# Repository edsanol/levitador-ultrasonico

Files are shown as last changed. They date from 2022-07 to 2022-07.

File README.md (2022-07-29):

# levitador-ultrasonico

El presente proyecto expone el diseño y la construcción un levitador capaz de hacer 
suspender partículas en el aire a través del principio de las ondas 
electromagnéticas, en este caso, las ondas acústicas mediante transductores 
ultrasónicos; con este principio, una partícula se levitará en contra de la fuerza de 
gravedad por medio de la presión sónica generada y alcanzará el equilibrio al 
contrarrestasen las ondas estacionarias. Además de esto, mediante un sistema de 
control clásico discreto, se realizará control de posición de las partículas en dos 
dimensiones (X, Z) al posicionar dos levitadores perpendicularmente haciendo 
necesario que el centroide de ambos sea común y se hará monitorización a través 
de un sistema HMI usando una cámara y visión artificial, quien detectara la posición 
de la partícula en las dos dimensiones. 

El proyecto inicia con el estudio del fenómeno detrás que la levitación acústica, 
dando a entender el por qué y las condiciones para hacer levitar objetos de mayor 
tamaño, seguidamente de esto, se diseña el modelado en donde se observa el 
posicionamiento de los transductores y las cotas del prototipo, a continuación, se 
realizan las pruebas de levitación de partículas en el prototipo. Una de las secciones 
fundamentales para el control de posición de partículas, es la implementación de la 
visión artificial, responsable de localizar y calcular la posición de la partícula los ejes 
X y Z; por último, se implementa un control clásico PID para controlar la posición de 
las partículas en el levitador que será supervisado por una interfaz humano maquina 
HMI.

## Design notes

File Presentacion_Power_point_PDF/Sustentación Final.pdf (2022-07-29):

# DESARROLLO DE UN SISTEMA DE CONTROL DE POSICIÓN DE PARTÍCULAS CON VISIÓN ARTIFICIAL EN UN LEVITADOR DE ONDAS ULTRASÓNICAS

# Autor: EDINAEL SANGUINO OLIVARES Tutor: M.Sc. OSCAR MANUEL DUQUE SUAREZ

# OBJETIVOS

1

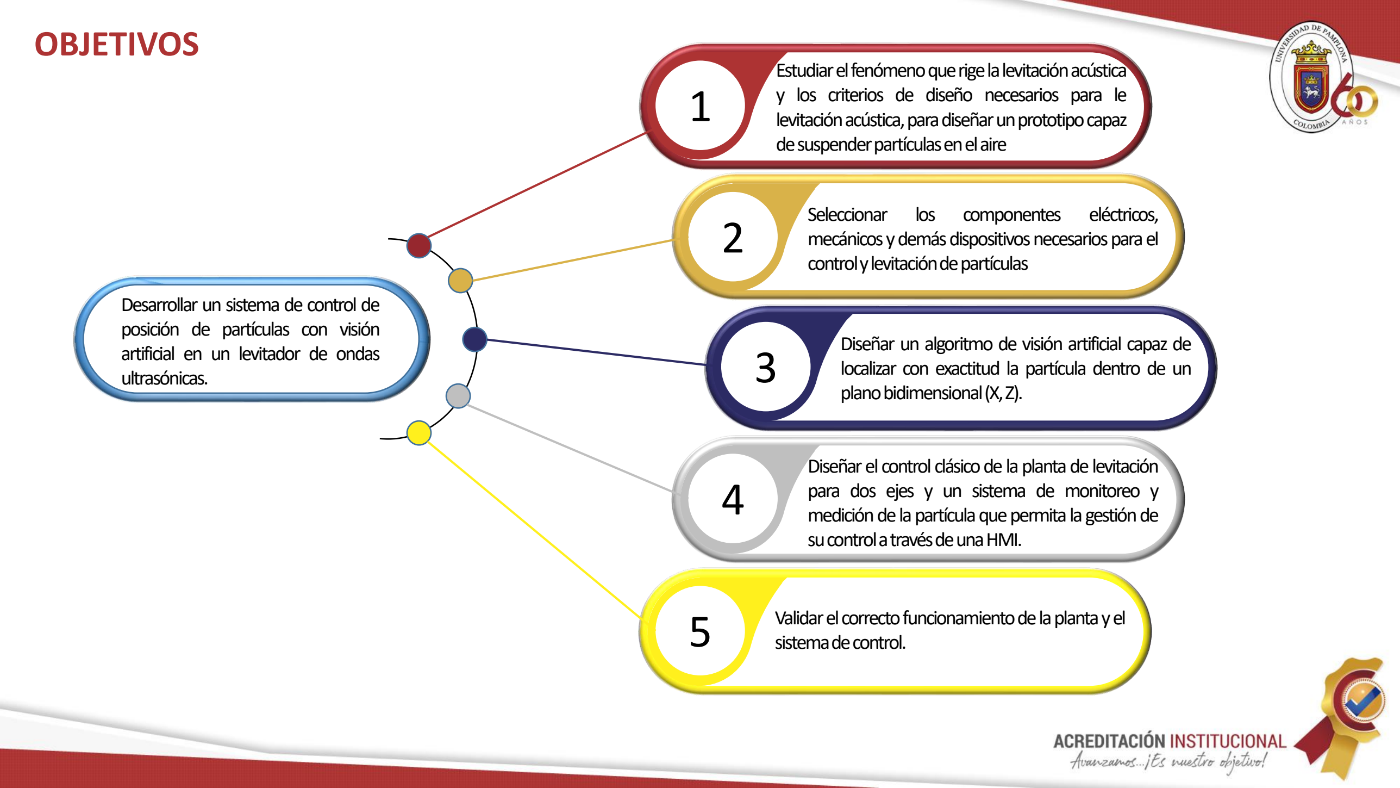
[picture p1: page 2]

### Desarrollar un sistema de control de posición de partículas con visión artificial en un levitador de ondas

ultrasónicas.

### Estudiarelfenómenoquerigelalevitaciónacústica y los criterios de diseño necesarios para le levitaciónacústica,paradiseñarunprototipocapaz desuspenderpartículasenelaire

Seleccionar | los | componentes | eléctricos,

### mecánicos ydemásdispositivosnecesariosparael controlylevitacióndepartículas

### Diseñar un algoritmo de visión artificial capaz de localizar con exactitud la partícula dentro de un

planobidimensional(X,Z).

### Diseñar el control clásicode la planta de levitación para dos ejes y un sistema de monitoreo y medicióndelapartículaquepermita la gestiónde

sucontrolatravésdeunaHMI.

### Validarelcorrectofuncionamientodelaplantayel

sistemadecontrol.

2

3

4

5

# Objetivo 1. Estudio del fenómeno que rige la levitación acústica para el diseño del prototipo de levitación

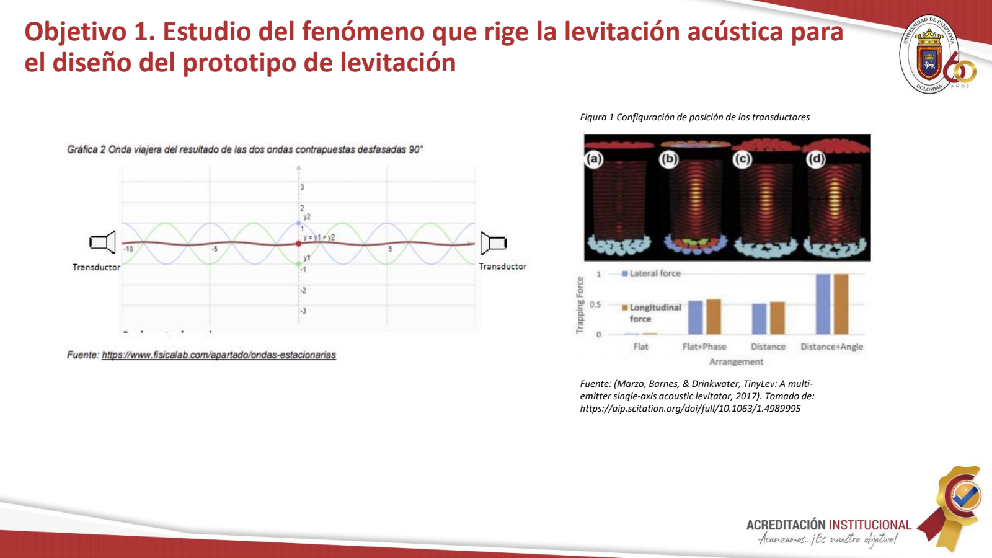
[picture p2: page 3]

Fuente: (Marzo, Barnes, & Drinkwater, TinyLev: A multiemitter single-axis acoustic levitator, 2017). Tomado de: https://aip.scitation.org/doi/full/10.1063/1.4989995

Figura 1 Configuración de posición de los transductores

# Objetivo 1. Estudio del fenómeno que rige la levitación acústica para el diseño del prototipo de levitación

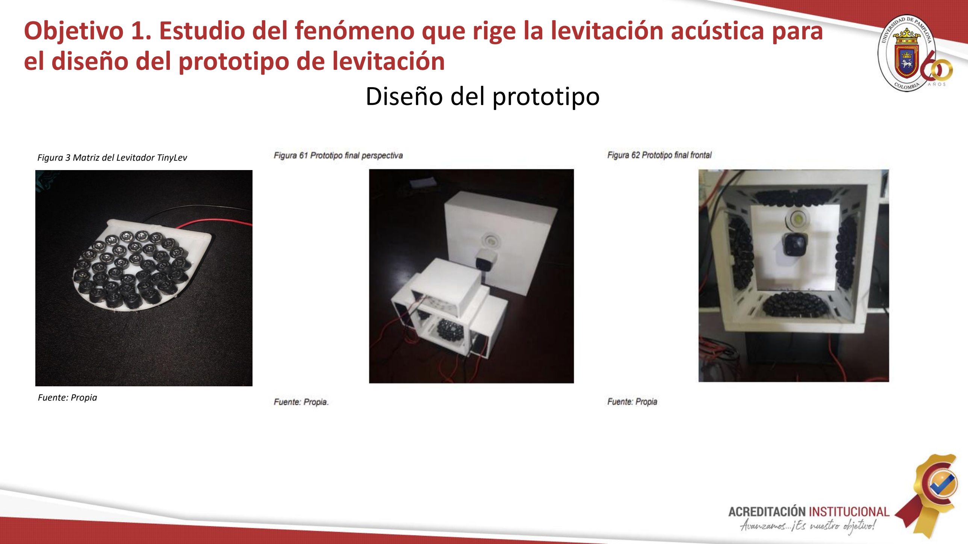
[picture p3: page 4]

# Diseño del prototipo

Fuente: Propia

Figura 3 Matriz del Levitador TinyLev

# Objetivo 2. Selección de componentes

# Metodología

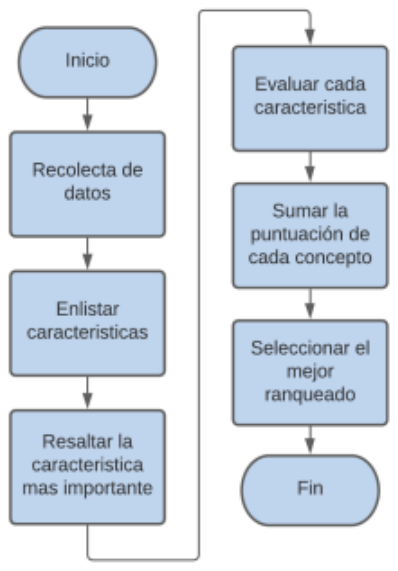
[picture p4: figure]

# Objetivo 2. Selección de componentes

Selección del microprocesador | Tarjeta de control de los transductores

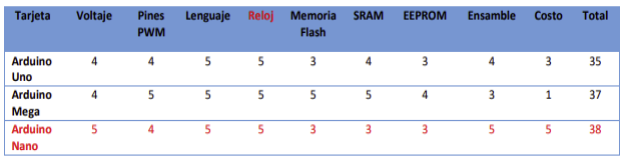
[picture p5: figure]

# Puente H para la potencia de los transductores

# Objetivo 2. Selección de componentes

Selección de la pantalla LCD | Cámara

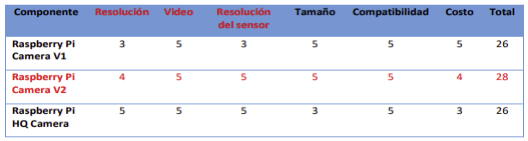
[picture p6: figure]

# Microcontrolador para el algoritmo de control

# Objetivo 3. Algoritmo de visión artificial

# Matriz de perspectiva

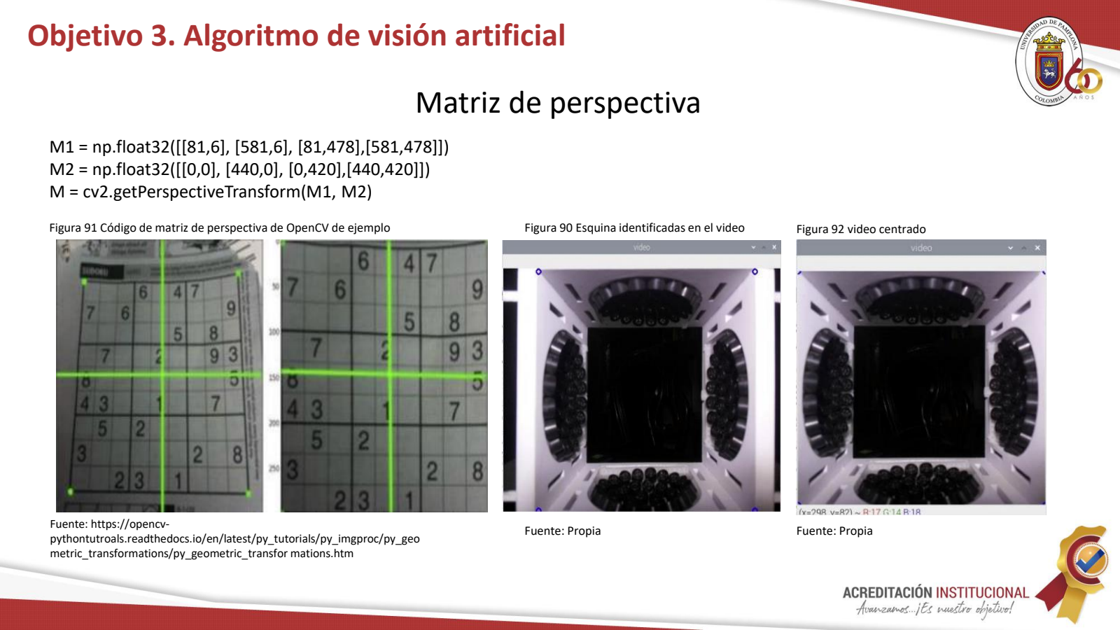
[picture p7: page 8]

Figura 91 Código de matriz de perspectiva de OpenCV de ejemplo

Fuente: https://opencvpythontutroals.readthedocs.io/en/latest/py_tutorials/py_imgproc/py_geometric_transformations/py_geometric_transfor mations.htm

Figura 90 Esquina identificadas en el video

Fuente: Propia | Fuente: Propia

Figura 92 video centrado

## M1 = np.float32([[81,6], [581,6], [81,478],[581,478]]) M2 = np.float32([[0,0], [440,0], [0,420],[440,420]]) M = cv2.getPerspectiveTransform(M1, M2)

# Objetivo 3. Algoritmo de visión artificial

# Filtro de la partícula por color

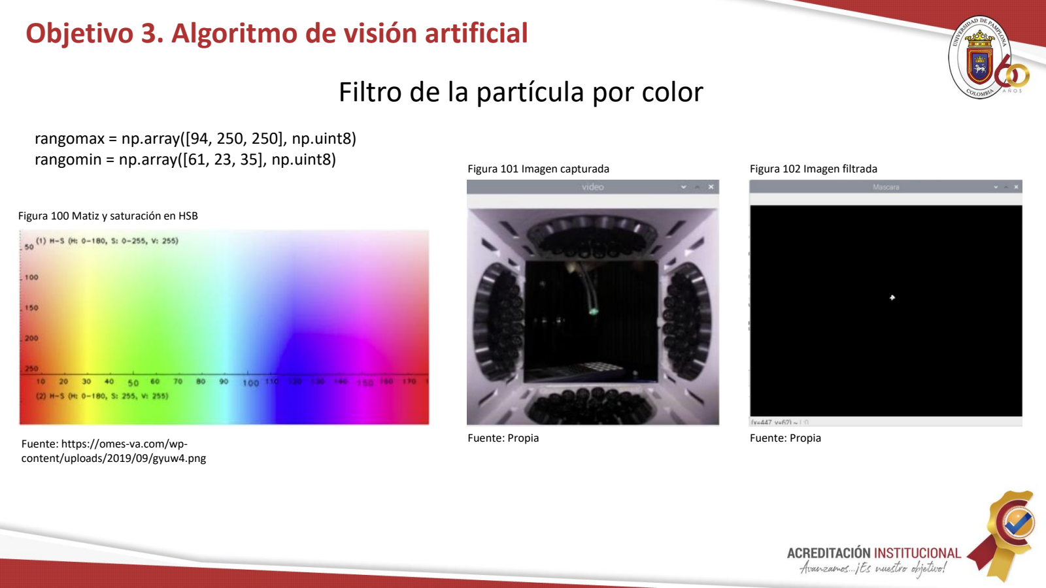
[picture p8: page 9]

Figura 100 Matiz y saturación en HSB

Figura 101 Imagen capturada | Figura 102 Imagen filtrada

Fuente: https://omes-va.com/wpcontent/uploads/2019/09/gyuw4.png

Fuente: Propia | Fuente: Propia

## rangomax = np.array([94, 250, 250], np.uint8) rangomin = np.array([61, 23, 35], np.uint8)

# Objetivo 3. Algoritmo de visión artificial

Figura 103 Ubicación de la partícula en pixeles

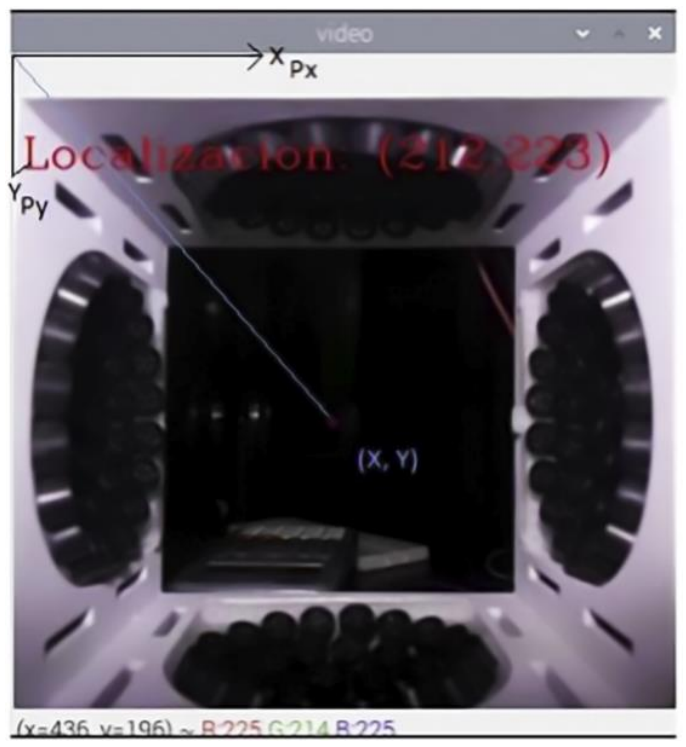
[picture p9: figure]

Fuente: Propia

## Vxmm = 110mm / 440px = 0.25mm

## Vymm = 105mm / 420px = 0.25mm

# Objetivo 3. Algoritmo de visión artificial

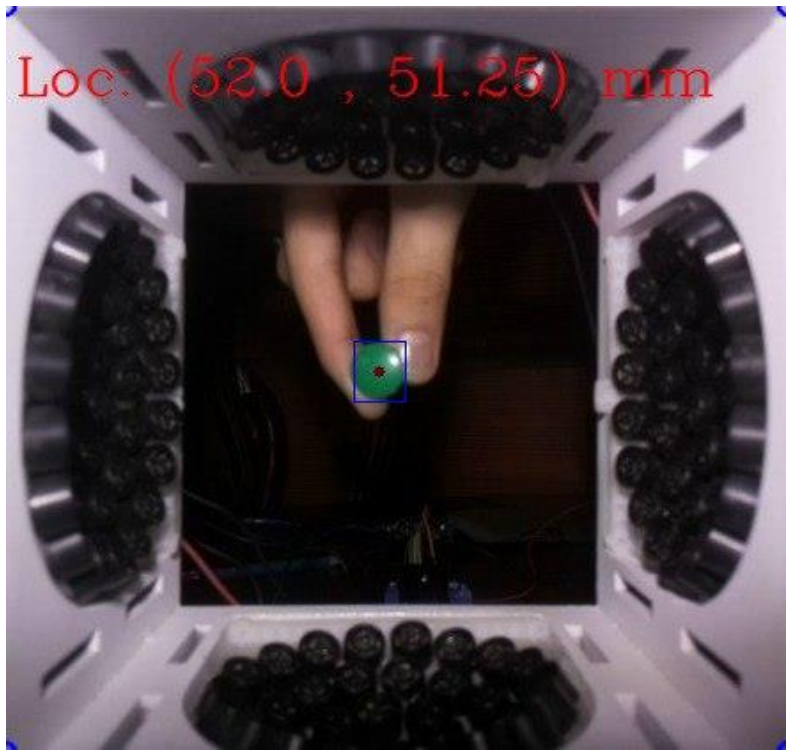
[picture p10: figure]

# Objetivo 4. Control de posición de la partícula en el levitador

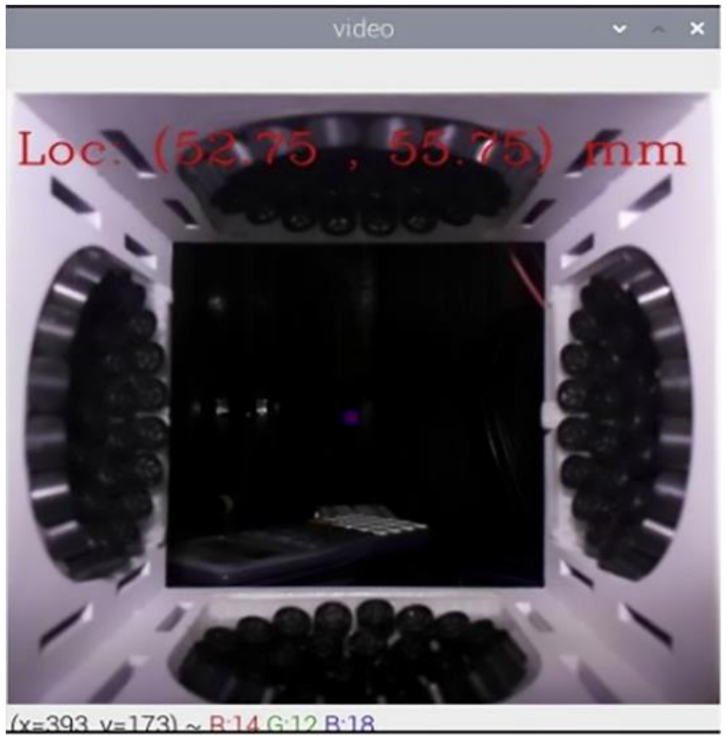
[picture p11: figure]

# Generación de la señal de 40 KHZ

static byte animation[N_FRAMES][N_DIVS] = {{0x5,0x5,0x5,0x5,0x5,0x5,0x5,0x5,0x5,0x5,0x5,0x5,0xa,0xa,0xa,0xa,0xa,0xa,0xa,0xa,0xa,0xa,0xa,0xa}, {0x9,0x5,0x5,0x5,0x5,0x5,0x5,0x5,0x5,0x5,0x5,0x5,0x6,0xa,0xa,0xa,0xa,0xa,0xa,0xa,0xa,0xa,0xa,0xa}, {0x9,0x9,0x5,0x5,0x5,0x5,0x5,0x5,0x5,0x5,0x5,0x5,0x6,0x6,0xa,0xa,0xa,0xa,0xa,0xa,0xa,0xa,0xa,0xa}, {0x9,0x9,0x9,0x5,0x5,0x5,0x5,0x5,0x5,0x5,0x5,0x5,0x6,0x6,0x6,0xa,0xa,0xa,0xa,0xa,0xa,0xa,0xa,0xa}, {0x9,0x9,0x9,0x9,0x5,0x5,0x5,0x5,0x5,0x5,0x5,0x5,0x6,0x6,0x6,0x6,0xa,0xa,0xa,0xa,0xa,0xa,0xa,0xa}, {0x9,0x9,0x9,0x9,0x9,0x5,0x5,0x5,0x5,0x5,0x5,0x5,0x6,0x6,0x6,0x6,0x6,0xa,0xa,0xa,0xa,0xa,0xa,0xa}, {0x9,0x9,0x9,0x9,0x9,0x9,0x5,0x5,0x5,0x5,0x5,0x5,0x6,0x6,0x6,0x6,0x6,0x6,0xa,0xa,0xa,0xa,0xa,0xa}, {0x9,0x9,0x9,0x9,0x9,0x9,0x9,0x5,0x5,0x5,0x5,0x5,0x6,0x6,0x6,0x6,0x6,0x6,0x6,0xa,0xa,0xa,0xa,0xa}, {0x9,0x9,0x9,0x9,0x9,0x9,0x9,0x9,0x5,0x5,0x5,0x5,0x6,0x6,0x6,0x6,0x6,0x6,0x6,0x6,0xa,0xa,0xa,0xa}, {0x9,0x9,0x9,0x9,0x9,0x9,0x9,0x9,0x9,0x5,0x5,0x5,0x6,0x6,0x6,0x6,0x6,0x6,0x6,0x6,0x6,0xa,0xa,0xa}, {0x9,0x9,0x9,0x9,0x9,0x9,0x9,0x9,0x9,0x9,0x5,0x5,0x6,0x6,0x6,0x6,0x6,0x6,0x6,0x6,0x6,0x6,0xa,0xa}, {0x9,0x9,0x9,0x9,0x9,0x9,0x9,0x9,0x9,0x9,0x9,0x5,0x6,0x6,0x6,0x6,0x6,0x6,0x6,0x6,0x6,0x6,0x6,0xa}, {0x9,0x9,0x9,0x9,0x9,0x9,0x9,0x9,0x9,0x9,0x9,0x9,0x6,0x6,0x6,0x6,0x6,0x6,0x6,0x6,0x6,0x6,0x6,0x6}, {0x5,0x9,0x9,0x9,0x9,0x9,0x9,0x9,0x9,0x9,0x9,0x9,0xa,0x6,0x6,0x6,0x6,0x6,0x6,0x6,0x6,0x6,0x6,0x6}, {0x5,0x5,0x9,0x9,0x9,0x9,0x9,0x9,0x9,0x9,0x9,0x9,0xa,0xa,0x6,0x6,0x6,0x6,0x6,0x6,0x6,0x6,0x6,0x6}, {0x5,0x5,0x5,0x9,0x9,0x9,0x9,0x9,0x9,0x9,0x9,0x9,0xa,0xa,0xa,0x6,0x6,0x6,0x6,0x6,0x6,0x6,0x6,0x6}, {0x5,0x5,0x5,0x5,0x9,0x9,0x9,0x9,0x9,0x9,0x9,0x9,0xa,0xa,0xa,0xa,0x6,0x6,0x6,0x6,0x6,0x6,0x6,0x6}, {0x5,0x5,0x5,0x5,0x5,0x9,0x9,0x9,0x9,0x9,0x9,0x9,0xa,0xa,0xa,0xa,0xa,0x6,0x6,0x6,0x6,0x6,0x6,0x6}, {0x5,0x5,0x5,0x5,0x5,0x5,0x9,0x9,0x9,0x9,0x9,0x9,0xa,0xa,0xa,0xa,0xa,0xa,0x6,0x6,0x6,0x6,0x6,0x6}, {0x5,0x5,0x5,0x5,0x5,0x5,0x5,0x9,0x9,0x9,0x9,0x9,0xa,0xa,0xa,0xa,0xa,0xa,0xa,0x6,0x6,0x6,0x6,0x6}, {0x5,0x5,0x5,0x5,0x5,0x5,0x5,0x5,0x9,0x9,0x9,0x9,0xa,0xa,0xa,0xa,0xa,0xa,0xa,0xa,0x6,0x6,0x6,0x6}, {0x5,0x5,0x5,0x5,0x5,0x5,0x5,0x5,0x5,0x9,0x9,0x9,0xa,0xa,0xa,0xa,0xa,0xa,0xa,0xa,0xa,0x6,0x6,0x6}, {0x5,0x5,0x5,0x5,0x5,0x5,0x5,0x5,0x5,0x5,0x9,0x9,0xa,0xa,0xa,0xa,0xa,0xa,0xa,0xa,0xa,0xa,0x6,0x6}, {0x5,0x5,0x5,0x5,0x5,0x5,0x5,0x5,0x5,0x5,0x5,0x9,0xa,0xa,0xa,0xa,0xa,0xa,0xa,0xa,0xa,0xa,0xa,0x6}};

Gráfica 5 Señal de salida de la matriz animation

Fuente: Propia.

Fuente: (Marzo, Barnes, & Drinkwater, TinyLev: A multiemitter single-axis acoustic levitator, 2017). Tomado de: https://aip.scitation.org/doi/full/10.1063/1.4989995

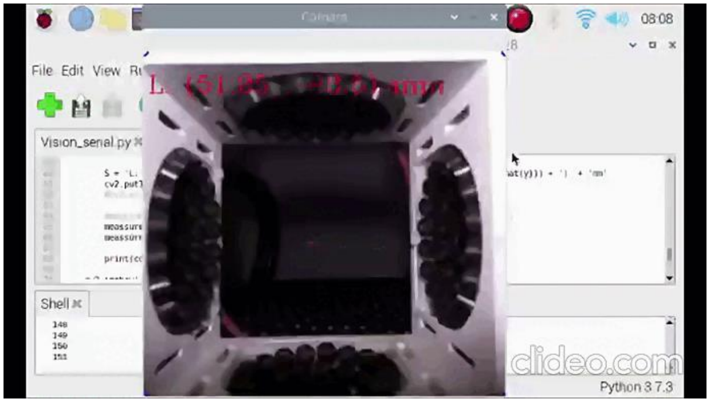
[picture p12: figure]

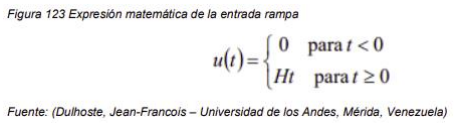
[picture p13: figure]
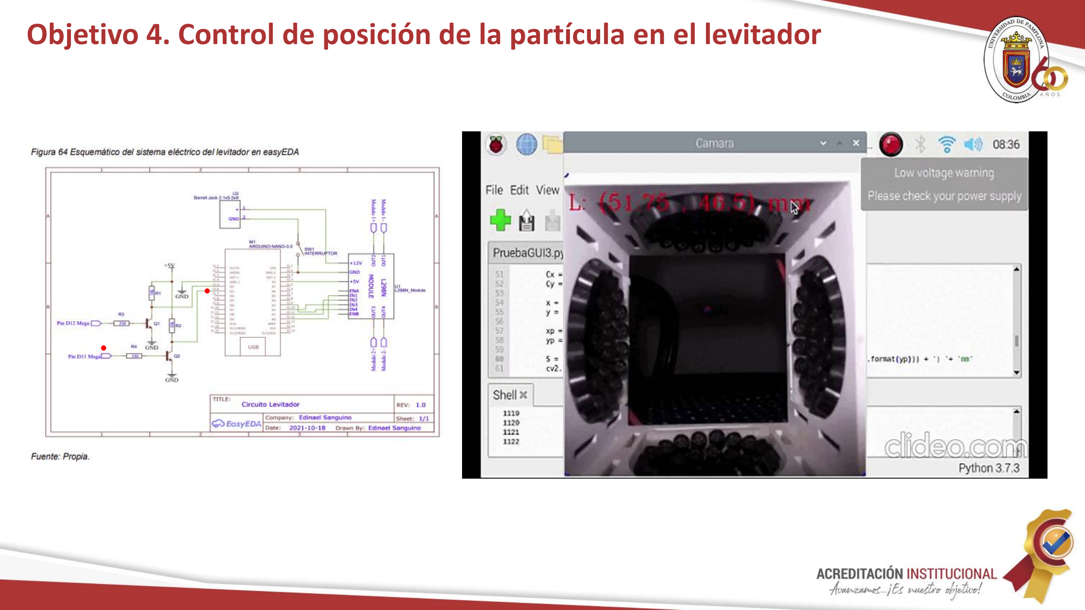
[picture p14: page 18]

# Identificación del sistema de control

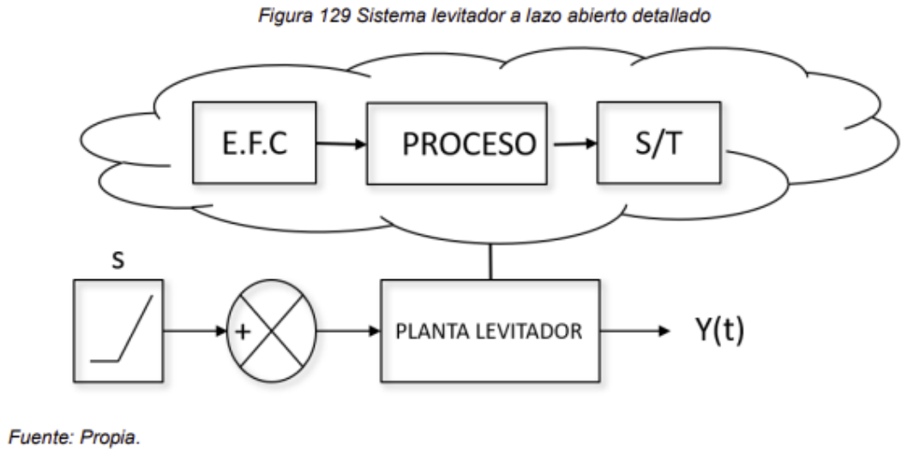
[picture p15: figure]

# Identificación del sistema de control

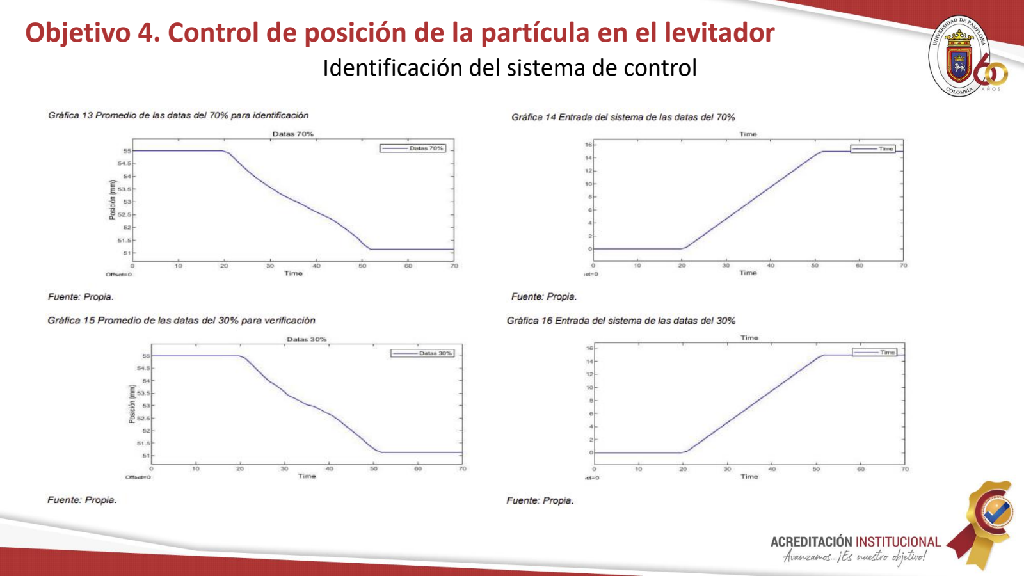
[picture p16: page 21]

# Identificación del sistema de control

# Sintonización del controlador método manual

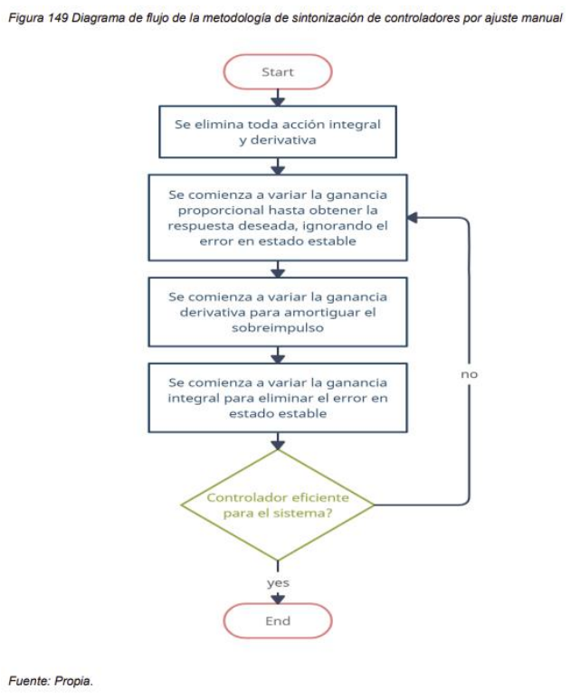
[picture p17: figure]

Evans, W. R. Graphical Analysis of Control Systems. AIEE Trans. Part. II, 1948, 69, pp. 547-551

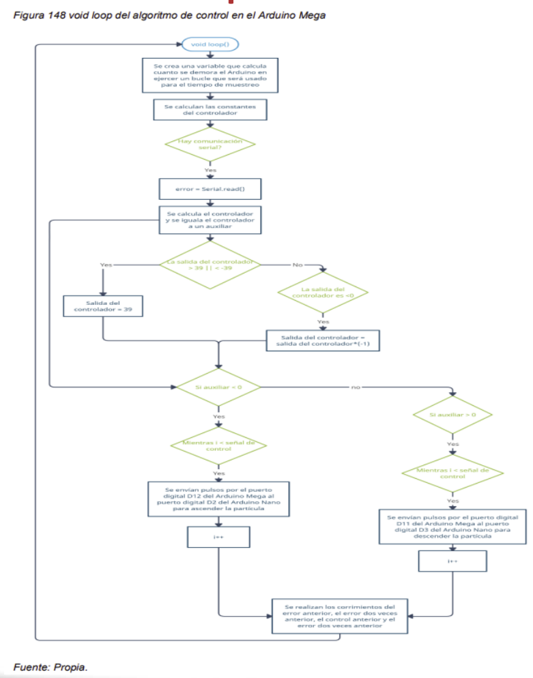
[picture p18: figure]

# Sintonización del controlador método manual

## Módulo vertical

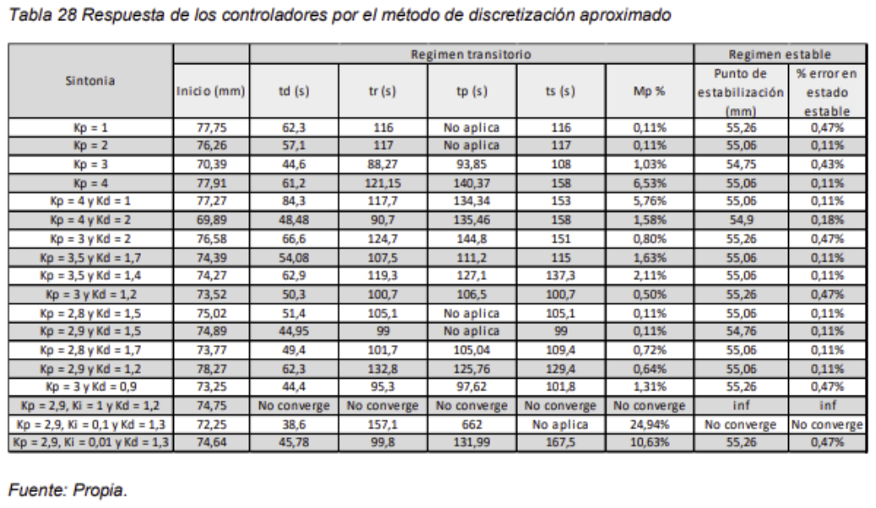
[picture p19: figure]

## U(k) = C0. e(k) + C1. e(k − 1) + C2. e(k − 2)

# Sintonización del controlador método manual

## Módulo vertical

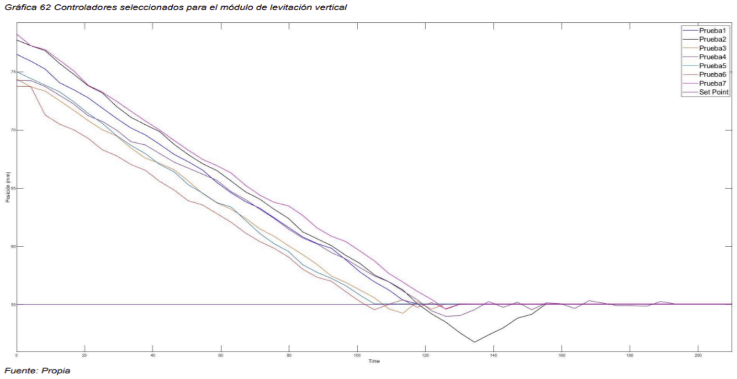
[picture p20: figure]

# Sintonización del controlador método manual

## Módulo vertical

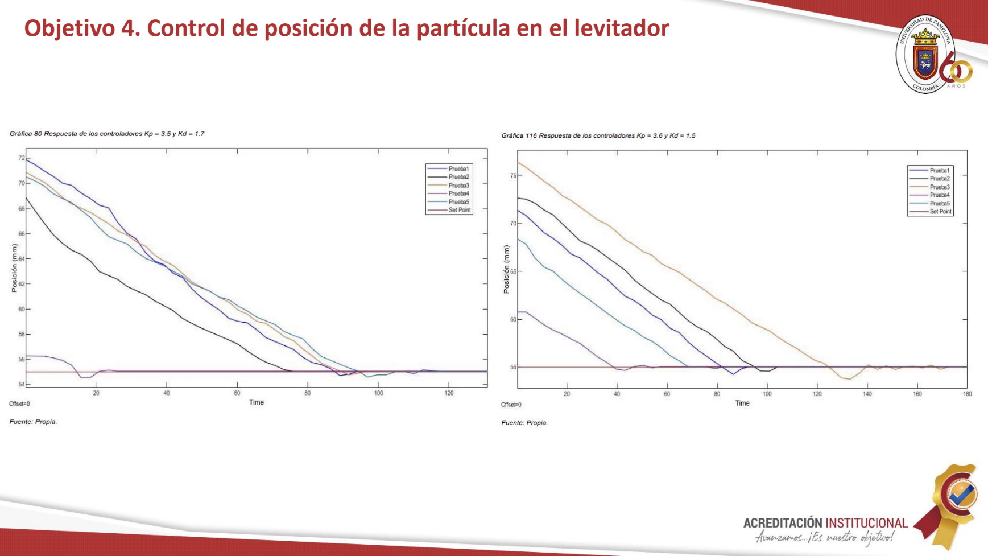
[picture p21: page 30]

# Sintonización del controlador método manual

## Módulo Horizontal

# Sintonización del controlador método manual

## Módulo Horizontal

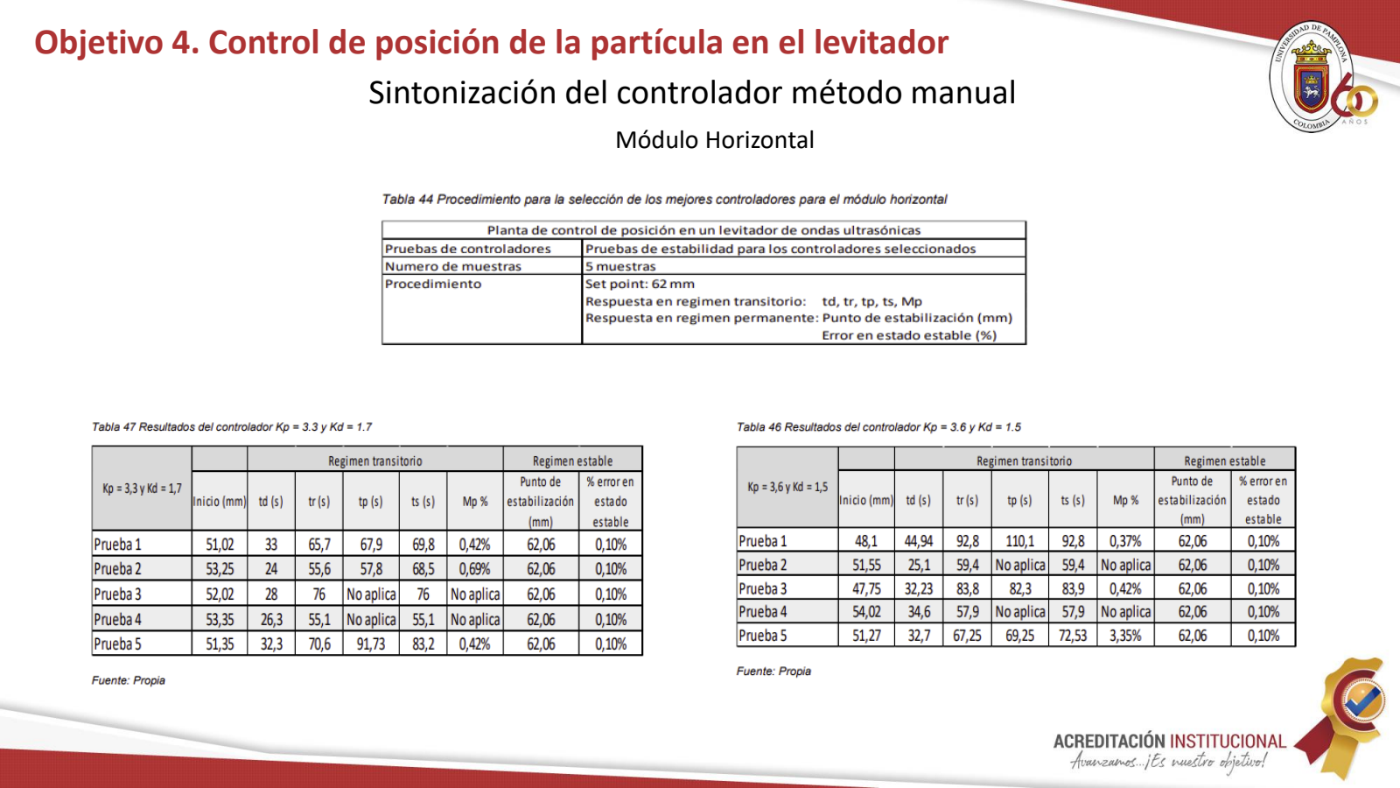
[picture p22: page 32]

# Pantalla HMI

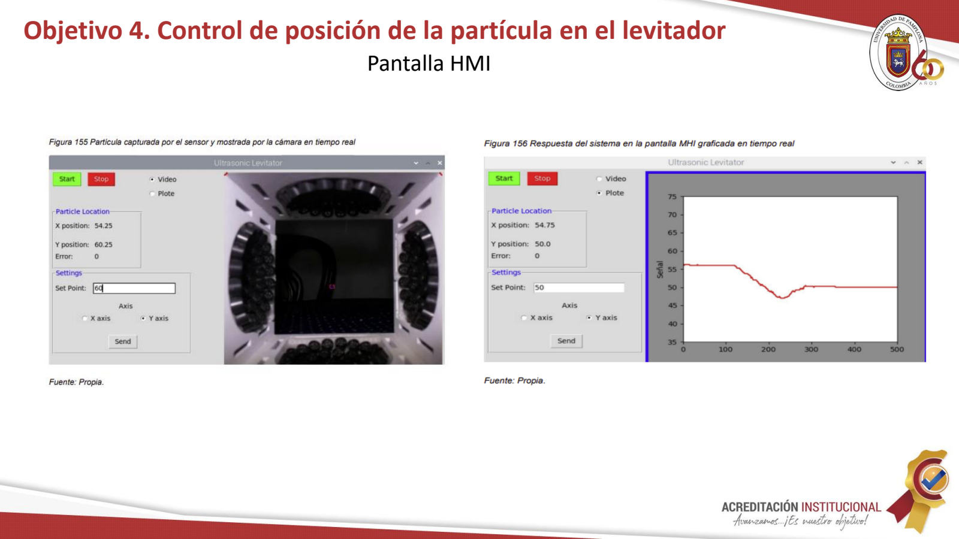
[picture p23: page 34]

# Objetivo 5. Validación del funcionamiento del sistema de control y robustez del controlador

# Análisis de robustez del controlador horizontal

## Kp = 4.1 y Kd = 0.4

# Objetivo 5. Validación del funcionamiento del sistema de control y robustez del controlador

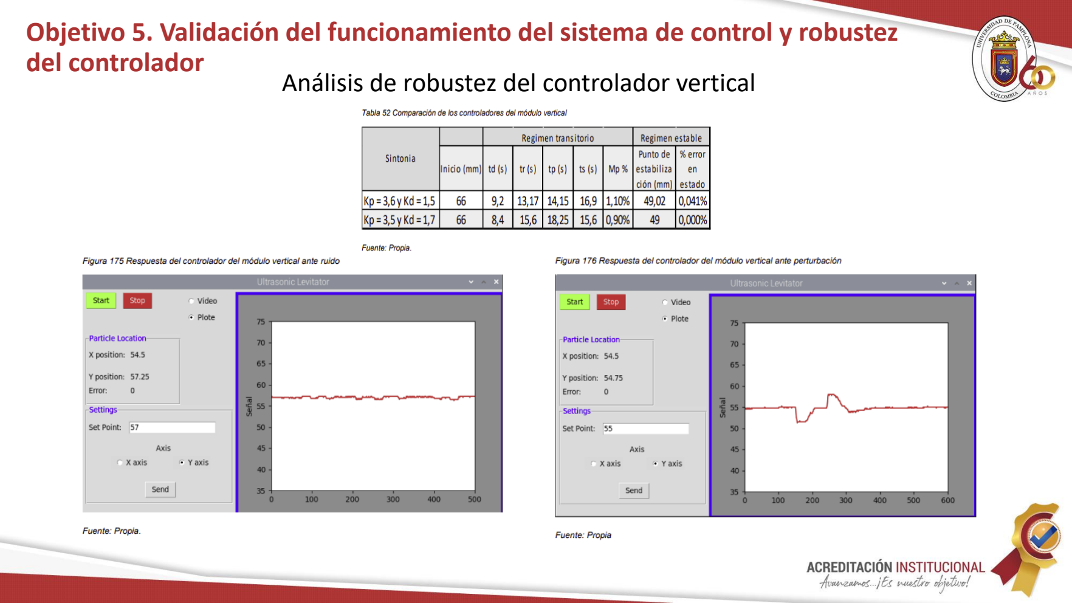
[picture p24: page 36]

# Análisis de robustez del controlador vertical

# Conclusiones

- Como puede apreciarse en la figura 119, es evidente la complejidad descrita en el diagrama de flujo de esta figura en la que puede observarse que se requiere la comunicación entre 5 tarjetas microcontroladoras para el funcionamiento de los dos módulos de la planta de levitación ultrasónica (X, Y), más sin embargo, no solo existen la comunicación serial, la comunicación I2C, entre otros protocolos, sino que simplemente con enviar pulsos de la salida de un controlador a la entrada de otro controlador, también puede realizarse comunicación no solo de forma asertiva sino que además, representa un altísimo ahorro de tiempo en donde leer un puerto físico le representa a un Arduino con un cristal de 16 MHz la inversión de tiempo de 62.5 µs. Gracias a este método de comunicación no convencional, se logró generar una señal PWM de 40 KHz y modificar el ciclo útil de esta señal en un Arduino como se puede observar en la figura 112. Esto no hubiera sido posible implementando un protocolo de comunicación estandarizado.
- Además de la necesidad de generar una señal PWM de 40 KHz para el funcionamiento de la partícula, es necesario variar el ciclo útil del PWM generado para lograr desplazar la partícula dentro del levitador, conforme se vaya variando el PWM, esta tarea es imposible realizarla implementando la instrucción analogWrite de Arduino para modificar el PWM, ya que se requerirían de muchas líneas de código de esta instrucción para variar al PWM necesario y múltiples condicionales para seleccionar cada uno. En la gráfica 5, se observa una señal generada por medio de una matriz, esta matriz es la encargada de variar el ciclo útil de la señal PWM sin perder su frecuencia. Con esto se puede concluir que existen métodos de generación de señales PWM y variar su ciclo útil mucho más eficientes y de mayor frecuencia que las ofrecidas por el foro oficial de Arduino.
- En la grafica 22 se puede apreciar la salida del sistema en lazo abierto al ser sometido a una entrada de tipo rampa, en donde su salida de respuesta demuestra que se trata de un sistema no lineal que no puede ser descrito por una función de transferencia, aun con esta característica se sintoniza un controlador PID clásico lineal y como se observa en la grafica 80, la grafica 116, la grafica 137 y la grafica 143, se logra converger el sistema en el valor del set point ingresado con buenas respuestas en régimen transitorio y permanente, lo que permite concluir que el controlador PID aunque es lineal, puede controlar sistemas que no sean fuertemente no lineales. Esto es debido a que el objetivo principal del controlador clásico PID es mantener el sistema en una posición de referencia indicada y ser capaz de aceptar nuevos valores de referencia. Ya si la referencia es una trayectoria, el controlador PID por si solo seria incapaz de seguir la trayectoria.

# Recomendaciones

- No fue posible obtener la función de transferencia de la planta de levitación ultrasónica, pero si fue sencillo encontrar la ecuación que define la posición de la partícula respecto a la entrada del sistema, por lo que se recomienda en estudios futuros, realizar métodos de control avanzado para el control de la posición de la partícula en los levitadores ultrasónicos.
- Actualmente se han realizado nuevas investigaciones sobre la levitación de objetos con la acústica, en donde se ha logrado levitar objetos de diámetros grandes que se consideraban imposibles de suspender con las ondas de sonido. Se sugiere indagar sobre estas investigaciones (son citadas en el libro de la tesis) para realizar la construcción de un prototipo que permita la levitación de objetos de tamaño mayor a la longitud de onda de sonido generada y realizar el control de posición de objetos siguiendo la metodología de esta investigación.
- Si se desea aumentar la resolución del sensor, se sugiere usar una pantalla con mayor resolución en pixeles a la utilizada en esta investigación.

# Formando líderes para la construcción de un nuevo país en paz

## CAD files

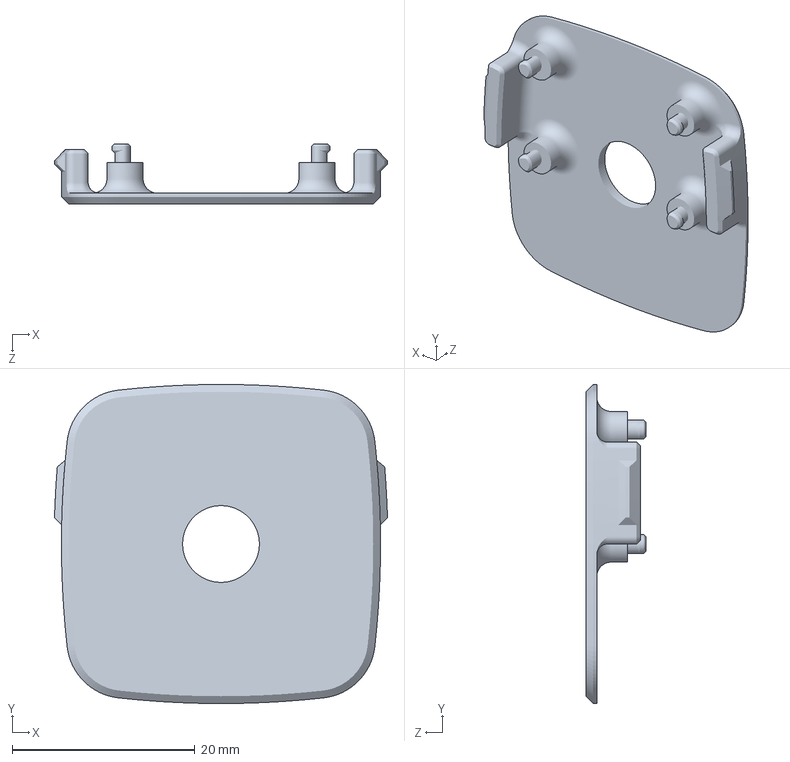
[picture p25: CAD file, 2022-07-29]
Anexos/Anexo A/Construccion de la planta/Camara/Mounting Plate.SLDPRT
36.4 x 34.9 x 6.60 mm

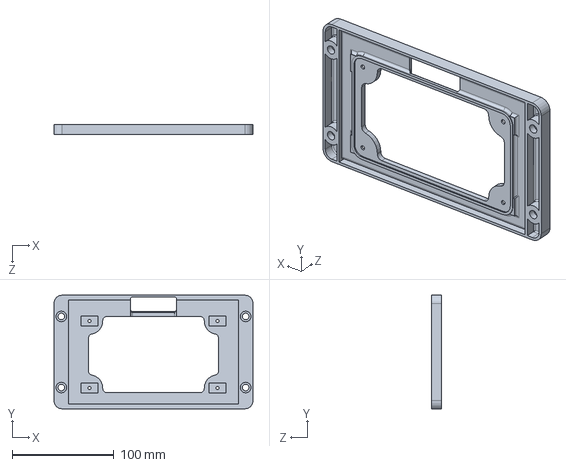
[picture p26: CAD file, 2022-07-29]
Anexos/Anexo A/Construccion de la planta/Pantalla HMI/Screen Base.SLDPRT
196.0 x 112.0 x 10.0 mm

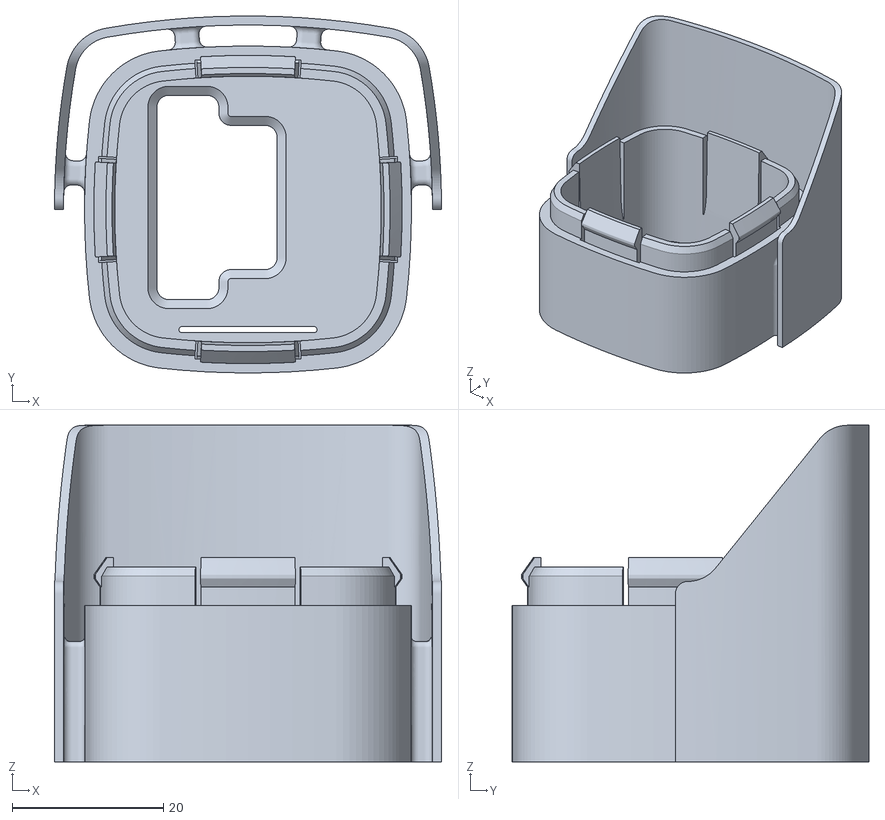
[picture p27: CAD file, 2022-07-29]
Anexos/Anexo A/Construccion de la planta/Camara/Pieza2.STL
51.1 x 47.1 x 44.5

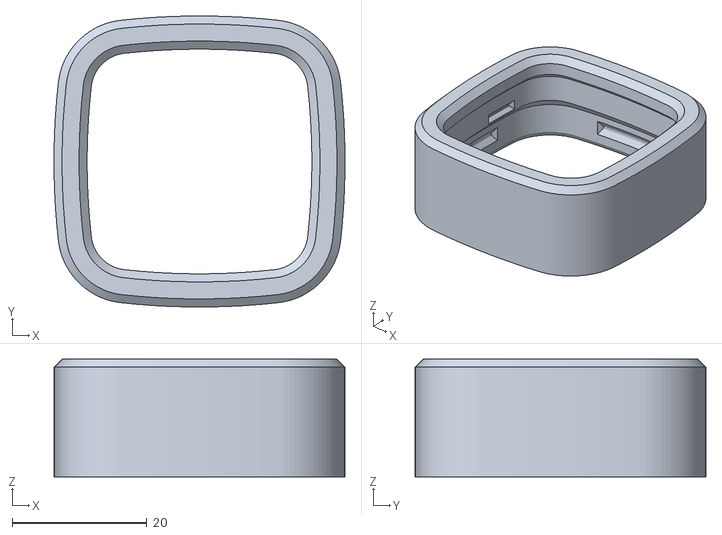
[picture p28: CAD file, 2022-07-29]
Anexos/Anexo A/Construccion de la planta/Camara/Pieza1.STL
43.2 x 43.2 x 17.5

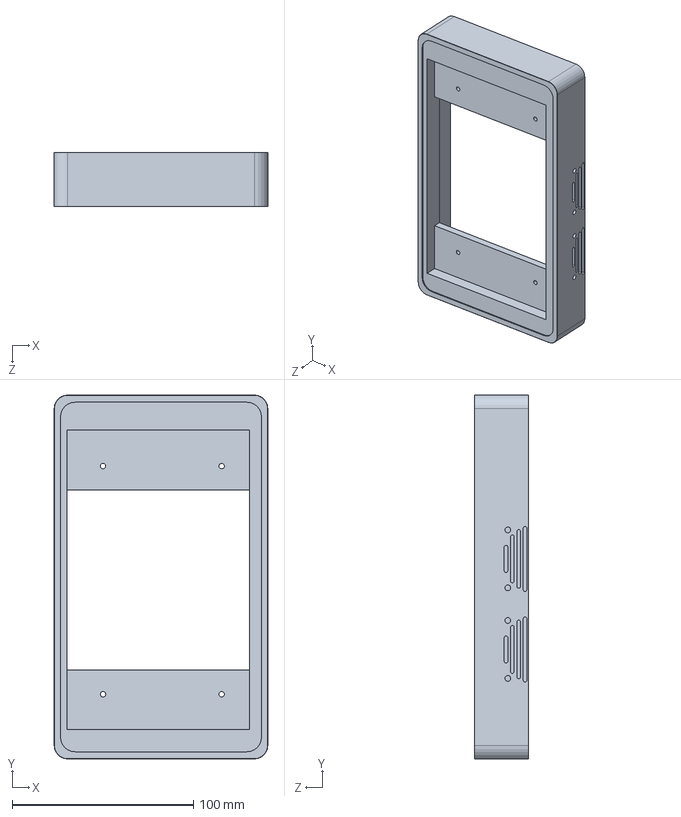
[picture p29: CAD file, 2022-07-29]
Anexos/Anexo A/Construccion de la planta/Pantalla HMI/Top Half v1.SLDPRT
118.0 x 201.0 x 30.0 mm

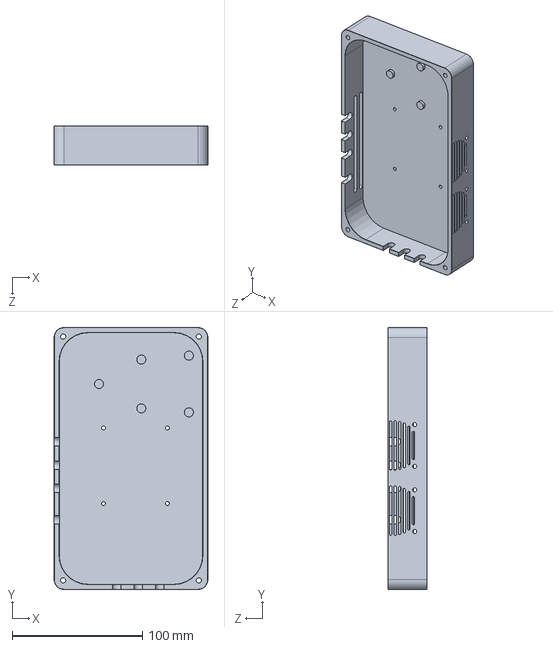
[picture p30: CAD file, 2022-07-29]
Anexos/Anexo A/Construccion de la planta/Pantalla HMI/Bottom Half v1.SLDPRT
118.0 x 201.0 x 30.0 mm

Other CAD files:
Anexos/Anexo A/Construccion de la planta/Pantalla HMI/Base Imprimir.STL
Anexos/Anexo A/Construccion de la planta/Camara/Pieza3.STL
Anexos/Anexo A/Construccion de la planta/Camara/Housing Front.SLDPRT
Anexos/Anexo A/Construccion de la planta/Camara/Housing Rear.SLDPRT
Anexos/Anexo A/Construccion de la planta/Pantalla HMI/Screen Base.STL

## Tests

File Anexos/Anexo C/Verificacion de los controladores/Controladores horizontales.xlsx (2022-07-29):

C1 | C2 | C3 | C4 | Time | VF1 | Time | VF2 | Time | VF3 | Time | VF4
51.25 | 52.25 | 52.25 | 60.50 | 0 | 52.25 | 0 | 52.00 | 0 | 52.25 | 0 | 50.50
52.50 | 52.50 | 53.25 | 60.50 | 1 | 52.25 | 1 | 51.50 | 1 | 52.25 | 1 | 50.25 | Sintonia |  | Regimen transitorio |  |  |  |  | Regimen estable
54.25 | 54.25 | 54.50 | 58.75 | 2 | 51.00 | 2 | 50.25 | 2 | 51.00 | 2 | 48.25 |  | Inicio (mm) | td (s) | tr (s) | tp (s) | ts (s) | Mp % | Punto de estabilización (mm) | % error en estado estable
55.75 | 56.00 | 56.75 | 57.50 | 3 | 49.25 | 3 | 48.50 | 3 | 49.00 | 3 | 47.75 | Kp = 3,6 y Kd = 1,5 | 48 | 8.62 | 15.08 | 16.6 | 17.3 | 0.40% | 62.942 | 0.092%
57.75 | 57.75 | 58.00 | 55.25 | 4 | 48.00 | 4 | 48.25 | 4 | 48.00 | 4 | 48.00 | Kp = 3,3 y Kd = 1,7 | 48 | 9.1 | 16.43 | 26.25 | oscilante | 0.80% | 62.93 | 0.110%
59.75 | 58.75 | 60.00 | 53.75 | 5 | 48.00 | 5 | 48.25 | 5 | 48.00 | 5 | 48.00 | Kp = 3,8 y Kd = 1 | 48 | 8.5 | 14.1 | 26.11 | 14.1 | 0.40% | 62.89 | 0.170%
61.25 | 61.00 | 61.50 | 51.75 | 6 | 48.00 | 6 | 48.25 | 6 | 48.00 | 6 | 48.00 | Kp = 4,1 y Kd = 0,4 | 48 | 6.93 | 11.46 | 12.35 | 13.6 | 2.70% | 62.944 | 0.088%
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

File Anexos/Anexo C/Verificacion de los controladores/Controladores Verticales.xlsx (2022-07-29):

C1 | C2 | Time | VF1 | Time | VF2
51.75 | 62.75 | 0 | 62.75 | 0 | 67.25
51.50 | 62.25 | 1 | 62.75 | 1 | 67.25 | Sintonia |  | Regimen transitorio |  |  |  |  | Regimen estable
50.00 | 60.75 | 2 | 64.25 | 2 | 66.75 |  | Inicio (mm) | td (s) | tr (s) | tp (s) | ts (s) | Mp % | Punto de estabilización (mm) | % error en estado estable
48.25 | 59.25 | 3 | 66.25 | 3 | 66.25 | Kp = 3,6 y Kd = 1,5 | 66 | 9.2 | 13.17 | 14.15 | 16.9 | 1.10% | 49.02 | 0.041%
47.00 | 57.5 | 4 | 66.00 | 4 | 65.75 | Kp = 3,5 y Kd = 1,7 | 66 | 8.4 | 15.6 | 18.25 | 15.6 | 0.90% | 49 | 0.000%
46.75 | 56.25 | 5 | 66.00 | 5 | 66.00
47.00 | 54.5 | 6 | 66.00 | 6 | 66.00
47.00 | 53.5 | 7 | 65.75 | 7 | 66.00
47.00 | 52.5 | 8 | 66.25 | 8 | 65.50
46.75 | 50.75 | 9 | 66.00 | 9 | 64.00
47.00 | 49.5 | 10 | 66.00 | 10 | 62.75
47.00 | 47.75 | 11 | 64.75 | 11 | 61.00
47.25 | 47.25 | 12 | 63.25 | 12 | 59.75
46.75 | 47.0 | 13 | 60.25 | 13 | 58.00
47.00 | 47.0 | 14 | 57.75 | 14 | 56.75
47.75 | 47.0 | 15 | 56.25 | 15 | 56.00
49.25 | 47.0 | 16 | 53.75 | 16 | 54.25
50.75 | 47.0 | 17 | 51.25 | 17 | 53.00
51.75 | 47.0 | 18 | 49.00 | 18 | 51.50
53.50 | 47.0 | 19 | 48.25 | 19 | 50.00
54.25 | 47.0 | 20 | 49.25 | 20 | 49.50
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

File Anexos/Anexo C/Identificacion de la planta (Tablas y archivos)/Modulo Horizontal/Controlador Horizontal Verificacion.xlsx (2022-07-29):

P = 4; D = 1 |  |  |  |  |  |  |  |  |  | P = 3,6; D = 1,5 |  |  |  |  |  |  |  |  |  | P = 3,3; D = 1,7 |  |  |  |  |  |  |  |  |  | P = 3,7; D = 1,3 |  |  |  |  |  |  |  |  |  | P = 3,8; D = 1
Tiempo | Data 1 | Tiempo | Data 2 | Tiempo | Data 3 | Tiempo | Data 4 | Tiempo | Data 5 | Tiempo | Data 1 | Tiempo | Data 2 | Tiempo | Data 3 | Tiempo | Data 4 | Tiempo | Data 5 | Tiempo | Data 1 | Tiempo | Data 2 | Tiempo | Data 3 | Tiempo | Data 4 | Tiempo | Data 5 | Tiempo | Data 1 | Tiempo | Data 2 | Tiempo | Data 3 | Tiempo | Data 4 | Tiempo | Data 5 | Tiempo | Data 1 | Tiempo | Data 2 | Tiempo | Data 3 | Tiempo | Data 4 | Tiempo | Data 5
2.066 | 49.55 | 2.011 | 50.25 | 2.12 | 45.54 | 2.094 | 48.75 | 1.921 | 48.05 | 2.12 | 48.05 | 2.21 | 51.55 | 1.97 | 48.25 | 2.00 | 54.26 | 2.25 | 51.26 | 2.15 | 51.26 | 2.29 | 54.00 | 2.32 | 52.26 | 2.23 | 54.05 | 2.24 | 51.55 | 2.23 | 53.00 | 2.02 | 50.75 | 2.27 | 53.55 | 2.06 | 48.25 | 2.27 | 50.75 | 2.27 | 52.05 | 2.18 | 51.00 | 2.28 | 54.05 | 2.49 | 52.26 | 2.07 | 51.26
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

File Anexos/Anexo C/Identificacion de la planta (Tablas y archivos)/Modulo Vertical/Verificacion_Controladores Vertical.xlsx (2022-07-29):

P = 2 |  |  |  |  |  |  |  |  |  | P = 4; D = 1 |  |  |  |  |  |  |  |  |  | P = 3,5; D = 1,7 |  |  |  |  |  |  |  |  |  | P = 3,5; D = 1,4 |  |  |  |  |  |  |  |  |  | P = 2,8; D = 1,5 |  |  |  |  |  |  |  |  |  | P = 2,8; D = 1,7
Tiempo | Data 1 | Tiempo | Data 2 | Tiempo | Data 3 | Tiempo | Data 4 | Tiempo | Data 5 | Tiempo | Data 1 | Tiempo | Data 2 | Tiempo | Data 3 | Tiempo | Data 4 | Tiempo | Data 5 | Tiempo | Data 1 | Tiempo | Data 2 | Tiempo | Data 3 | Tiempo | Data 4 | Tiempo | Data 5 | Tiempo | Data 1 | Tiempo | Data 2 | Tiempo | Data 3 | Tiempo | Data 4 | Tiempo | Data 5 | Tiempo | Data 1 | Tiempo | Data 2 | Tiempo | Data 3 | Tiempo | Data 4 | Tiempo | Data 5 | Tiempo | Data 1 | Tiempo | Data 2
2.02 | 66.26 | 1.916 | 73.26 | 2.05 | 72.07 | 1.88 | 78.08 | 2.15 | 66.76 | 2.07 | 67.07 | 1.96 | 70.76 | 2.16 | 69.76 | 2.00 | 69.26 | 1.96 | 62.76 | 2.06 | 71.57 | 2.07 | 68.07 | 1.99 | 70.57 | 3.13 | 56.26 | 2.15 | 70.26 | 1.89 | 70.26 | 2.04 | 64.26 | 1.87 | 68.00 | 2.18 | 67.76 | 1.91 | 73.07 | 1.99 | 68.07 | 2.10 | 69.26 | 1.96 | 71.76 | 1.96 | 73.26 | 1.93 | 66.25 | 1.88 | 74.26 | 1.98 | 71.57
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

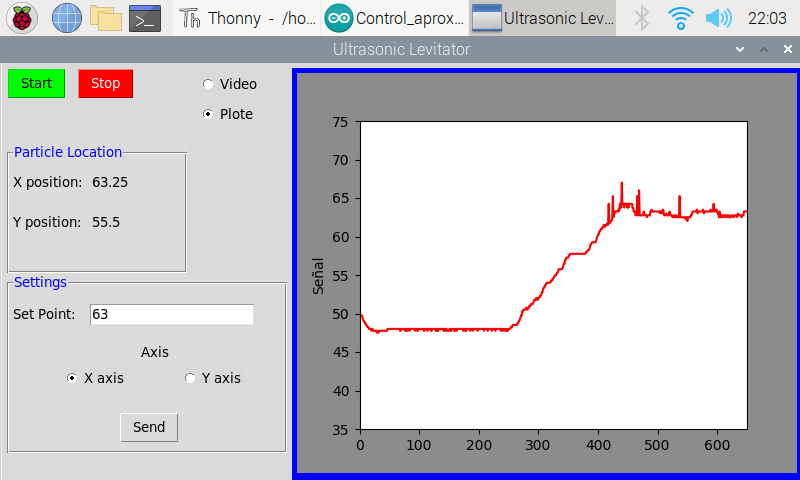
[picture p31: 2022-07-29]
Anexos/Anexo C/Verificacion de los controladores/Ruido y perturbacion horizontal/VF4/Captura de pantalla de 2021-11-12 22-03-02__VF4.png

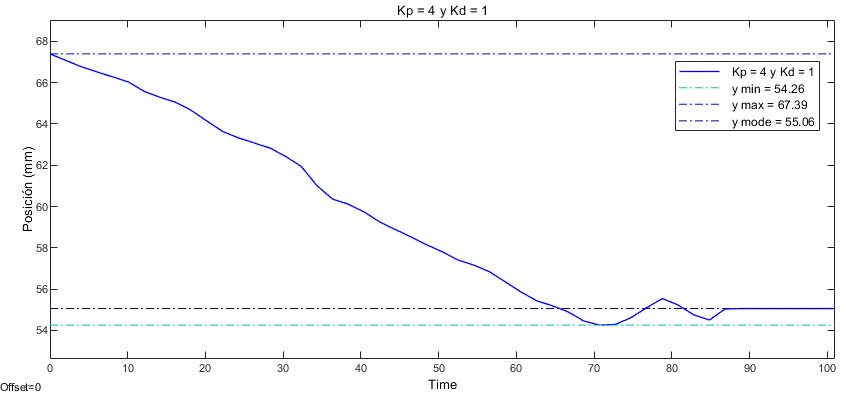
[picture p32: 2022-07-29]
Anexos/Anexo D/Modulo Vertical/Pruebas de controladores/Segundo controlador/prueba 1.jpg

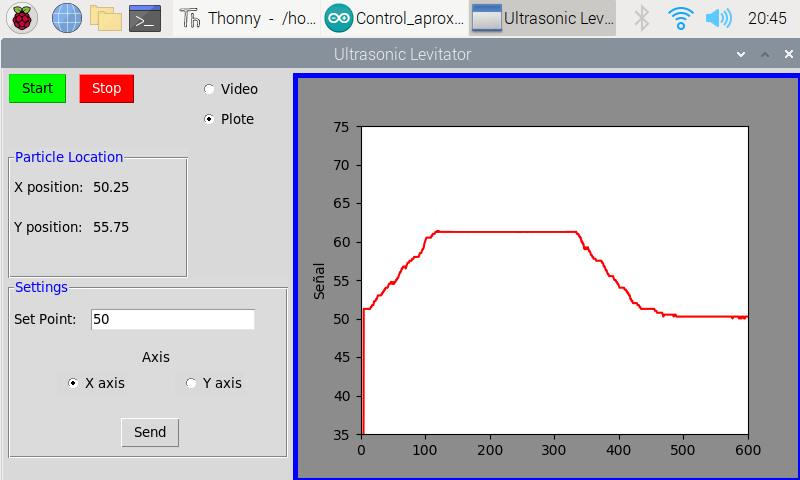
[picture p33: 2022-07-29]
Anexos/Anexo C/Verificacion de los controladores/Ruido y perturbacion horizontal/Primer controlador/Captura de pantalla de 2021-11-12 20-45-16VS.png

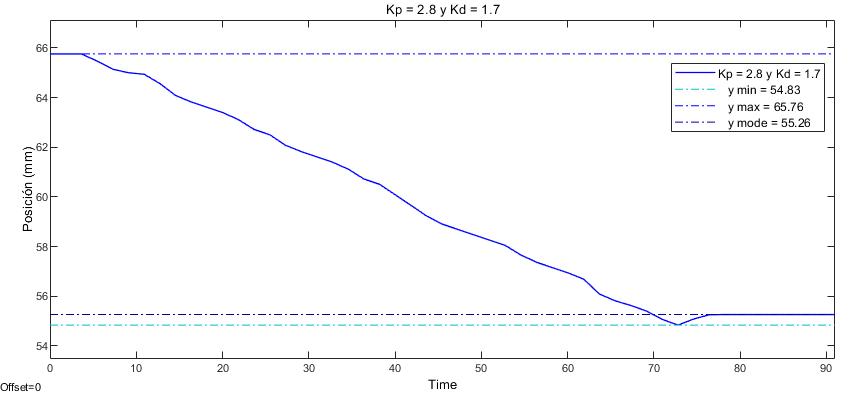
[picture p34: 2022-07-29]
Anexos/Anexo D/Modulo Vertical/Pruebas de controladores/Sexto controlador/prueba 4.jpg

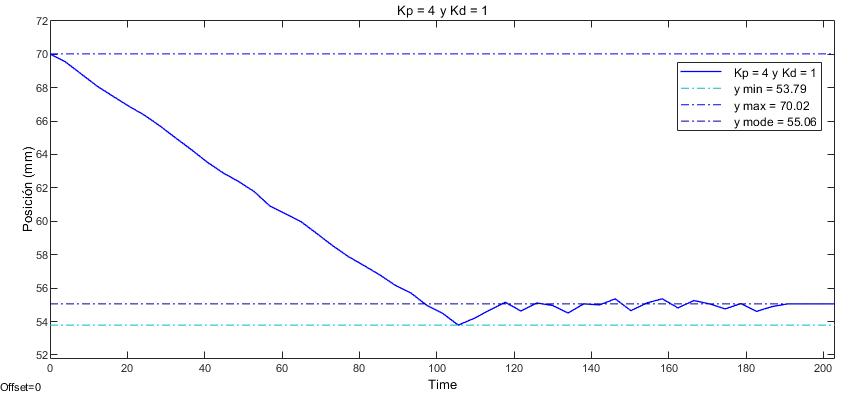
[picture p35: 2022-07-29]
Anexos/Anexo D/Modulo Vertical/Pruebas de controladores/Segundo controlador/prueba 3.jpg

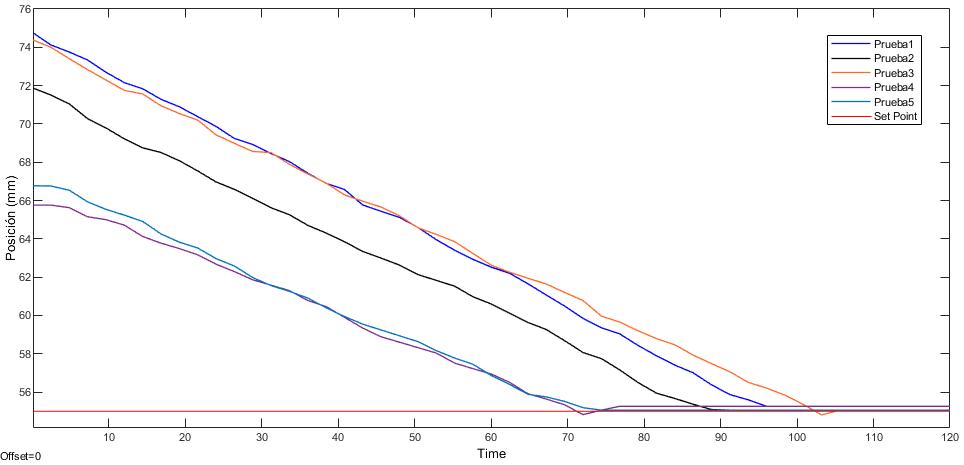
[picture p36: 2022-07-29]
Anexos/Anexo D/Modulo Vertical/Pruebas de controladores/Sexto controlador/prueba final.jpg

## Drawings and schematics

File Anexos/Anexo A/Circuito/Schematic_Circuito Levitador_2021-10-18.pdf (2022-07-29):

A | A

1

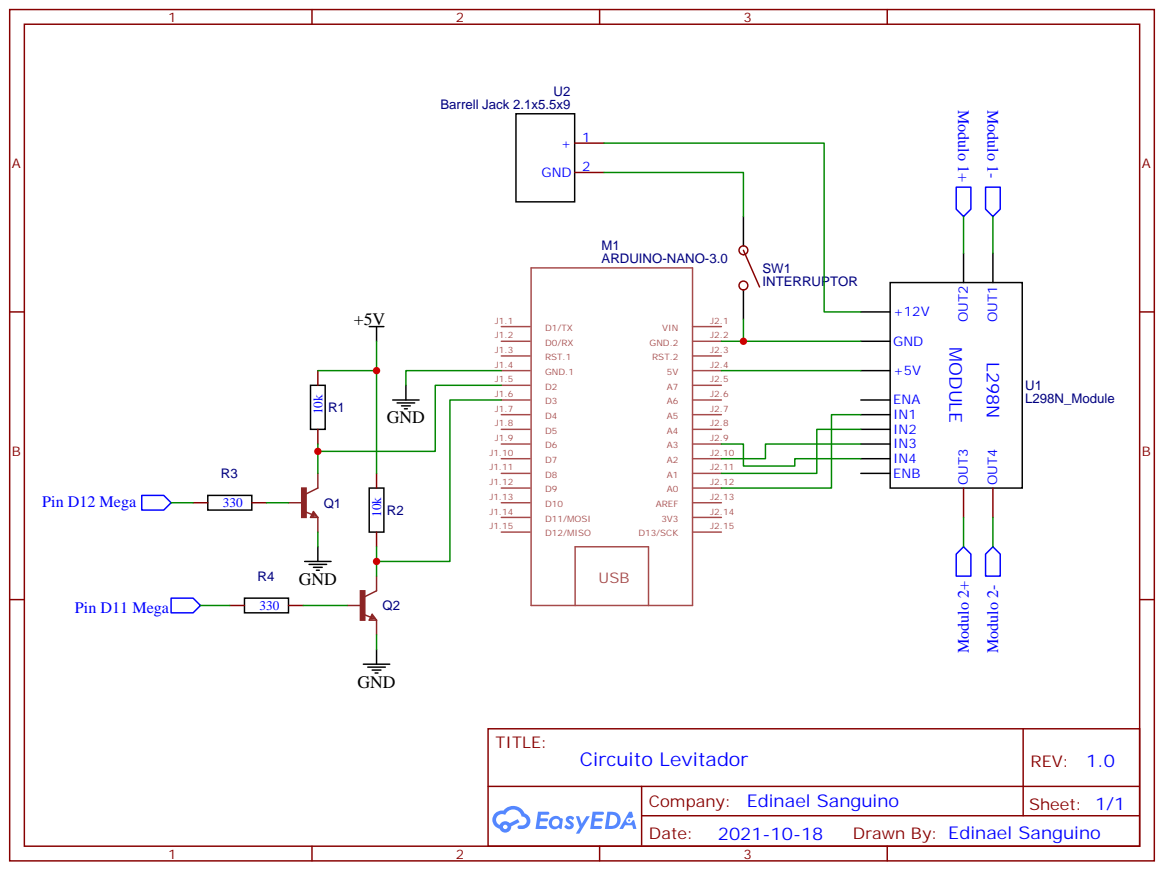
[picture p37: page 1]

Drawn By: Edinael Sanguino

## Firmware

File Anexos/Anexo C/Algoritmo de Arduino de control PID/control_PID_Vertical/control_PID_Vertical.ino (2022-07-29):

float SetPoint, Sv;
float e[3] = {0.0, 0.0, 0.0};
int u[2] = {0.0, 0.0};
int Aux, cont;
int up = 12;
int down = 11;
float Kp = 3.6;
float Ki = 0;
float Kd = 1.5;
float C0 = 0, C1 = 0, C2 = 0;
float tiempo, ts, timePrev;
float A_3 = 0;

void setup()
{
  pinMode(up, OUTPUT);
  pinMode(down, OUTPUT);
  Serial.begin(115200);
  tiempo = millis();
  delay(300);
}

void loop() {
  timePrev = tiempo;
  tiempo = millis();
  ts = (tiempo - timePrev) / 1000;
  
  C2 = (Ki*ts)/2;
  A_3 = Kd/ts;
  C0 = Kp+C2+A_3;
  C1 = C2+C2-A_3;
  
  if(Serial.available())
  {
    String c = Serial.readString();
    e[0] = c.toFloat();
    //Sv = c.toFloat();
    Serial.print("Valor: ");
    Serial.println(e[0]);
  }

  // Calculo del PID
  u[0] = C0*e[0]+C1*e[1]+C2*e[2];
  Aux = u[0];

  // Saturador
  if(u[0] > 39) u[0] = 39;
  if(u[0] < 0.0 && u[0] >= -39) u[0] = u[0]*-1;
  if(u[0] < -39) u[0] = 39;

  if(Aux < 0 && cont >= 2)
  {
    for(int i = 0; i < u[0]; i++)
    {
      if(Serial.available())
    {
      String c = Serial.readString();
      e[0] = c.toFloat();
      Serial.println(e[0]);
    }
      digitalWrite(up, HIGH);
      delay(400);
      digitalWrite(up, LOW);
      delay(10);
    }
      delay(10);
  }

  else if(Aux > 0 && cont >= 2)
  {
    for(int i = 0; i < u[0]; i++)
    {
      if(Serial.available())
    {
      String c = Serial.readString();
      e[0] = c.toFloat();
      Serial.println(e[0]);
    }
      digitalWrite(down, HIGH);
      delay(400);
      digitalWrite(down, LOW);
      delay(10);
    }
      delay(10);
  }

  // Corrimientos
  e[2] = e[1];
  e[1] = e[0];
  u[1] = u[0];

  Serial.print(u[0]);
  Serial.print("  ");
  Serial.print(e[0]);
  Serial.print("  ");
  Serial.print(Sv);
  Serial.print("  ");
  Serial.println(tiempo);

  delay(1500);
  cont++;
}

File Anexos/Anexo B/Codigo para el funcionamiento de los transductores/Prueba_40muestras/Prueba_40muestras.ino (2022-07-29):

#include <avr/sleep.h>
#include <avr/power.h>

#define N_PORTS 1 // Numero de puertos con los que se trabajara en la función macro
#define N_DIVS 40 // Numero de filas dentro de la matriz de animación
#define N_BUTTONS 6 // Numero de botones que pueden usarsen
#define STEP_SIZE 1 // Tamaño de cada paso
#define BUTTON_SENS 4000 // Sensibilidad del boton
#define N_FRAMES 40 // Numero de columnas de la matriz animación

#define WAIT_LOT(a) __asm__ __volatile__ ("nop"); __asm__ __volatile__ ("nop");  __asm__ __volatile__ ("nop");  __asm__ __volatile__ ("nop");  __asm__ __volatile__ ("nop");__asm__ __volatile__ ("nop");__asm__ __volatile__ ("nop")
#define WAIT_MID(a) __asm__ __volatile__ ("nop"); __asm__ __volatile__ ("nop");  __asm__ __volatile__ ("nop"); __asm__ __volatile__ ("nop"); __asm__ __volatile__ ("nop");__asm__ __volatile__ ("nop")
#define WAIT_LIT(a) __asm__ __volatile__ ("nop");  __asm__ __volatile__ ("nop");  __asm__ __volatile__ ("nop"); __asm__ __volatile__ ("nop")


#define OUTPUT_WAVE(pointer, d)  PORTC = pointer[d*N_PORTS + 0]



static byte frame = 0;
static byte animation[N_FRAMES][N_DIVS] = 
{{0x5,0x5,0x5,0x5,0x5,0x5,0x5,0x5,0x5,0x5,0x5,0x5,0x5,0x5,0x5,0x5,0x5,0x5,0x5,0x5,0xa,0xa,0xa,0xa,0xa,0xa,0xa,0xa,0xa,0xa,0xa,0xa,0xa,0xa,0xa,0xa,0xa,0xa,0xa,0xa},
{0x9,0x5,0x5,0x5,0x5,0x5,0x5,0x5,0x5,0x5,0x5,0x5,0x5,0x5,0x5,0x5,0x5,0x5,0x5,0x5,0x6,0xa,0xa,0xa,0xa,0xa,0xa,0xa,0xa,0xa,0xa,0xa,0xa,0xa,0xa,0xa,0xa,0xa,0xa,0xa},
{0x9,0x9,0x5,0x5,0x5,0x5,0x5,0x5,0x5,0x5,0x5,0x5,0x5,0x5,0x5,0x5,0x5,0x5,0x5,0x5,0x6,0x6,0xa,0xa,0xa,0xa,0xa,0xa,0xa,0xa,0xa,0xa,0xa,0xa,0xa,0xa,0xa,0xa,0xa,0xa},
{0x9,0x9,0x9,0x5,0x5,0x5,0x5,0x5,0x5,0x5,0x5,0x5,0x5,0x5,0x5,0x5,0x5,0x5,0x5,0x5,0x6,0x6,0x6,0xa,0xa,0xa,0xa,0xa,0xa,0xa,0xa,0xa,0xa,0xa,0xa,0xa,0xa,0xa,0xa,0xa},
{0x9,0x9,0x9,0x9,0x5,0x5,0x5,0x5,0x5,0x5,0x5,0x5,0x5,0x5,0x5,0x5,0x5,0x5,0x5,0x5,0x6,0x6,0x6,0x6,0xa,0xa,0xa,0xa,0xa,0xa,0xa,0xa,0xa,0xa,0xa,0xa,0xa,0xa,0xa,0xa},
{0x9,0x9,0x9,0x9,0x9,0x5,0x5,0x5,0x5,0x5,0x5,0x5,0x5,0x5,0x5,0x5,0x5,0x5,0x5,0x5,0x6,0x6,0x6,0x6,0x6,0xa,0xa,0xa,0xa,0xa,0xa,0xa,0xa,0xa,0xa,0xa,0xa,0xa,0xa,0xa},
{0x9,0x9,0x9,0x9,0x9,0x9,0x5,0x5,0x5,0x5,0x5,0x5,0x5,0x5,0x5,0x5,0x5,0x5,0x5,0x5,0x6,0x6,0x6,0x6,0x6,0x6,0xa,0xa,0xa,0xa,0xa,0xa,0xa,0xa,0xa,0xa,0xa,0xa,0xa,0xa},
{0x9,0x9,0x9,0x9,0x9,0x9,0x9,0x5,0x5,0x5,0x5,0x5,0x5,0x5,0x5,0x5,0x5,0x5,0x5,0x5,0x6,0x6,0x6,0x6,0x6,0x6,0x6,0xa,0xa,0xa,0xa,0xa,0xa,0xa,0xa,0xa,0xa,0xa,0xa,0xa},
{0x9,0x9,0x9,0x9,0x9,0x9,0x9,0x9,0x5,0x5,0x5,0x5,0x5,0x5,0x5,0x5,0x5,0x5,0x5,0x5,0x6,0x6,0x6,0x6,0x6,0x6,0x6,0x6,0xa,0xa,0xa,0xa,0xa,0xa,0xa,0xa,0xa,0xa,0xa,0xa},
{0x9,0x9,0x9,0x9,0x9,0x9,0x9,0x9,0x9,0x5,0x5,0x5,0x5,0x5,0x5,0x5,0x5,0x5,0x5,0x5,0x6,0x6,0x6,0x6,0x6,0x6,0x6,0x6,0x6,0xa,0xa,0xa,0xa,0xa,0xa,0xa,0xa,0xa,0xa,0xa},
{0x9,0x9,0x9,0x9,0x9,0x9,0x9,0x9,0x9,0x9,0x5,0x5,0x5,0x5,0x5,0x5,0x5,0x5,0x5,0x5,0x6,0x6,0x6,0x6,0x6,0x6,0x6,0x6,0x6,0x6,0xa,0xa,0xa,0xa,0xa,0xa,0xa,0xa,0xa,0xa},
{0x9,0x9,0x9,0x9,0x9,0x9,0x9,0x9,0x9,0x9,0x9,0x5,0x5,0x5,0x5,0x5,0x5,0x5,0x5,0x5,0x6,0x6,0x6,0x6,0x6,0x6,0x6,0x6,0x6,0x6,0x6,0xa,0xa,0xa,0xa,0xa,0xa,0xa,0xa,0xa},
{0x9,0x9,0x9,0x9,0x9,0x9,0x9,0x9,0x9,0x9,0x9,0x9,0x5,0x5,0x5,0x5,0x5,0x5,0x5,0x5,0x6,0x6,0x6,0x6,0x6,0x6,0x6,0x6,0x6,0x6,0x6,0x6,0xa,0xa,0xa,0xa,0xa,0xa,0xa,0xa},
{0x9,0x9,0x9,0x9,0x9,0x9,0x9,0x9,0x9,0x9,0x9,0x9,0x9,0x5,0x5,0x5,0x5,0x5,0x5,0x5,0x6,0x6,0x6,0x6,0x6,0x6,0x6,0x6,0x6,0x6,0x6,0x6,0x6,0xa,0xa,0xa,0xa,0xa,0xa,0xa},
{0x9,0x9,0x9,0x9,0x9,0x9,0x9,0x9,0x9,0x9,0x9,0x9,0x9,0x9,0x5,0x5,0x5,0x5,0x5,0x5,0x6,0x6,0x6,0x6,0x6,0x6,0x6,0x6,0x6,0x6,0x6,0x6,0x6,0x6,0xa,0xa,0xa,0xa,0xa,0xa},
{0x9,0x9,0x9,0x9,0x9,0x9,0x9,0x9,0x9,0x9,0x9,0x9,0x9,0x9,0x9,0x5,0x5,0x5,0x5,0x5,0x6,0x6,0x6,0x6,0x6,0x6,0x6,0x6,0x6,0x6,0x6,0x6,0x6,0x6,0x6,0xa,0xa,0xa,0xa,0xa},
{0x9,0x9,0x9,0x9,0x9,0x9,0x9,0x9,0x9,0x9,0x9,0x9,0x9,0x9,0x9,0x9,0x5,0x5,0x5,0x5,0x6,0x6,0x6,0x6,0x6,0x6,0x6,0x6,0x6,0x6,0x6,0x6,0x6,0x6,0x6,0x6,0xa,0xa,0xa,0xa},
{0x9,0x9,0x9,0x9,0x9,0x9,0x9,0x9,0x9,0x9,0x9,0x9,0x9,0x9,0x9,0x9,0x9,0x5,0x5,0x5,0x6,0x6,0x6,0x6,0x6,0x6,0x6,0x6,0x6,0x6,0x6,0x6,0x6,0x6,0x6,0x6,0x6,0xa,0xa,0xa},
{0x9,0x9,0x9,0x9,0x9,0x9,0x9,0x9,0x9,0x9,0x9,0x9,0x9,0x9,0x9,0x9,0x9,0x9,0x5,0x5,0x6,0x6,0x6,0x6,0x6,0x6,0x6,0x6,0x6,0x6,0x6,0x6,0x6,0x6,0x6,0x6,0x6,0x6,0xa,0xa},
{0x9,0x9,0x9,0x9,0x9,0x9,0x9,0x9,0x9,0x9,0x9,0x9,0x9,0x9,0x9,0x9,0x9,0x9,0x9,0x5,0x6,0x6,0x6,0x6,0x6,0x6,0x6,0x6,0x6,0x6,0x6,0x6,0x6,0x6,0x6,0x6,0x6,0x6,0x6,0xa},
{0x9,0x9,0x9,0x9,0x9,0x9,0x9,0x9,0x9,0x9,0x9,0x9,0x9,0x9,0x9,0x9,0x9,0x9,0x9,0x9,0x6,0x6,0x6,0x6,0x6,0x6,0x6,0x6,0x6,0x6,0x6,0x6,0x6,0x6,0x6,0x6,0x6,0x6,0x6,0x6},
{0x5,0x9,0x9,0x9,0x9,0x9,0x9,0x9,0x9,0x9,0x9,0x9,0x9,0x9,0x9,0x9,0x9,0x9,0x9,0x9,0xa,0x6,0x6,0x6,0x6,0x6,0x6,0x6,0x6,0x6,0x6,0x6,0x6,0x6,0x6,0x6,0x6,0x6,0x6,0x6},
{0x5,0x5,0x9,0x9,0x9,0x9,0x9,0x9,0x9,0x9,0x9,0x9,0x9,0x9,0x9,0x9,0x9,0x9,0x9,0x9,0xa,0xa,0x6,0x6,0x6,0x6,0x6,0x6,0x6,0x6,0x6,0x6,0x6,0x6,0x6,0x6,0x6,0x6,0x6,0x6},
{0x5,0x5,0x5,0x9,0x9,0x9,0x9,0x9,0x9,0x9,0x9,0x9,0x9,0x9,0x9,0x9,0x9,0x9,0x9,0x9,0xa,0xa,0xa,0x6,0x6,0x6,0x6,0x6,0x6,0x6,0x6,0x6,0x6,0x6,0x6,0x6,0x6,0x6,0x6,0x6},
{0x5,0x5,0x5,0x5,0x9,0x9,0x9,0x9,0x9,0x9,0x9,0x9,0x9,0x9,0x9,0x9,0x9,0x9,0x9,0x9,0xa,0xa,0xa,0xa,0x6,0x6,0x6,0x6,0x6,0x6,0x6,0x6,0x6,0x6,0x6,0x6,0x6,0x6,0x6,0x6},
{0x5,0x5,0x5,0x5,0x5,0x9,0x9,0x9,0x9,0x9,0x9,0x9,0x9,0x9,0x9,0x9,0x9,0x9,0x9,0x9,0xa,0xa,0xa,0xa,0xa,0x6,0x6,0x6,0x6,0x6,0x6,0x6,0x6,0x6,0x6,0x6,0x6,0x6,0x6,0x6},
{0x5,0x5,0x5,0x5,0x5,0x5,0x9,0x9,0x9,0x9,0x9,0x9,0x9,0x9,0x9,0x9,0x9,0x9,0x9,0x9,0xa,0xa,0xa,0xa,0xa,0xa,0x6,0x6,0x6,0x6,0x6,0x6,0x6,0x6,0x6,0x6,0x6,0x6,0x6,0x6},
{0x5,0x5,0x5,0x5,0x5,0x5,0x5,0x9,0x9,0x9,0x9,0x9,0x9,0x9,0x9,0x9,0x9,0x9,0x9,0x9,0xa,0xa,0xa,0xa,0xa,0xa,0xa,0x6,0x6,0x6,0x6,0x6,0x6,0x6,0x6,0x6,0x6,0x6,0x6,0x6},
{0x5,0x5,0x5,0x5,0x5,0x5,0x5,0x5,0x9,0x9,0x9,0x9,0x9,0x9,0x9,0x9,0x9,0x9,0x9,0x9,0xa,0xa,0xa,0xa,0xa,0xa,0xa,0xa,0x6,0x6,0x6,0x6,0x6,0x6,0x6,0x6,0x6,0x6,0x6,0x6},
{0x5,0x5,0x5,0x5,0x5,0x5,0x5,0x5,0x5,0x9,0x9,0x9,0x9,0x9,0x9,0x9,0x9,0x9,0x9,0x9,0xa,0xa,0xa,0xa,0xa,0xa,0xa,0xa,0xa,0x6,0x6,0x6,0x6,0x6,0x6,0x6,0x6,0x6,0x6,0x6},
{0x5,0x5,0x5,0x5,0x5,0x5,0x5,0x5,0x5,0x5,0x9,0x9,0x9,0x9,0x9,0x9,0x9,0x9,0x9,0x9,0xa,0xa,0xa,0xa,0xa,0xa,0xa,0xa,0xa,0xa,0x6,0x6,0x6,0x6,0x6,0x6,0x6,0x6,0x6,0x6},
{0x5,0x5,0x5,0x5,0x5,0x5,0x5,0x5,0x5,0x5,0x5,0x9,0x9,0x9,0x9,0x9,0x9,0x9,0x9,0x9,0xa,0xa,0xa,0xa,0xa,0xa,0xa,0xa,0xa,0xa,0xa,0x6,0x6,0x6,0x6,0x6,0x6,0x6,0x6,0x6},
{0x5,0x5,0x5,0x5,0x5,0x5,0x5,0x5,0x5,0x5,0x5,0x5,0x9,0x9,0x9,0x9,0x9,0x9,0x9,0x9,0xa,0xa,0xa,0xa,0xa,0xa,0xa,0xa,0xa,0xa,0xa,0xa,0x6,0x6,0x6,0x6,0x6,0x6,0x6,0x6},
{0x5,0x5,0x5,0x5,0x5,0x5,0x5,0x5,0x5,0x5,0x5,0x5,0x5,0x9,0x9,0x9,0x9,0x9,0x9,0x9,0xa,0xa,0xa,0xa,0xa,0xa,0xa,0xa,0xa,0xa,0xa,0xa,0xa,0x6,0x6,0x6,0x6,0x6,0x6,0x6},
{0x5,0x5,0x5,0x5,0x5,0x5,0x5,0x5,0x5,0x5,0x5,0x5,0x5,0x5,0x9,0x9,0x9,0x9,0x9,0x9,0xa,0xa,0xa,0xa,0xa,0xa,0xa,0xa,0xa,0xa,0xa,0xa,0xa,0xa,0x6,0x6,0x6,0x6,0x6,0x6},
{0x5,0x5,0x5,0x5,0x5,0x5,0x5,0x5,0x5,0x5,0x5,0x5,0x5,0x5,0x5,0x9,0x9,0x9,0x9,0x9,0xa,0xa,0xa,0xa,0xa,0xa,0xa,0xa,0xa,0xa,0xa,0xa,0xa,0xa,0xa,0x6,0x6,0x6,0x6,0x6},
{0x5,0x5,0x5,0x5,0x5,0x5,0x5,0x5,0x5,0x5,0x5,0x5,0x5,0x5,0x5,0x5,0x9,0x9,0x9,0x9,0xa,0xa,0xa,0xa,0xa,0xa,0xa,0xa,0xa,0xa,0xa,0xa,0xa,0xa,0xa,0xa,0x6,0x6,0x6,0x6},
{0x5,0x5,0x5,0x5,0x5,0x5,0x5,0x5,0x5,0x5,0x5,0x5,0x5,0x5,0x5,0x5,0x5,0x9,0x9,0x9,0xa,0xa,0xa,0xa,0xa,0xa,0xa,0xa,0xa,0xa,0xa,0xa,0xa,0xa,0xa,0xa,0xa,0x6,0x6,0x6},
{0x5,0x5,0x5,0x5,0x5,0x5,0x5,0x5,0x5,0x5,0x5,0x5,0x5,0x5,0x5,0x5,0x5,0x5,0x9,0x9,0xa,0xa,0xa,0xa,0xa,0xa,0xa,0xa,0xa,0xa,0xa,0xa,0xa,0xa,0xa,0xa,0xa,0xa,0x6,0x6},
{0x5,0x5,0x5,0x5,0x5,0x5,0x5,0x5,0x5,0x5,0x5,0x5,0x5,0x5,0x5,0x5,0x5,0x5,0x5,0x9,0xa,0xa,0xa,0xa,0xa,0xa,0xa,0xa,0xa,0xa,0xa,0xa,0xa,0xa,0xa,0xa,0xa,0xa,0xa,0x6}};

void setup()
{
   DDRC = 0b00001111;     //A0 a A3 son señales de salida
   PORTC = 0b00000000;    //Pines a nivel bajo
   
   pinMode(10, OUTPUT);       //pin 10 (B2) generará una señal 40KHz a sincronismo    
   pinMode(11, INPUT_PULLUP); //pin 11 (B3) es el sincronismo de entrada                  
   //IMPORTANTE tener conectado el pin 10 con el 11

   for (int i = 2; i < 8; ++i){   //pin 2 a 7 (D2 a D7) son entradas para los botones
    pinMode(i, INPUT_PULLUP); 
   }

  // Genera una señal de sincronismo de 40 KHz en el pin 10
  noInterrupts();           // dehabilita todas las interrupciones
  TCCR1A = bit (WGM10) | bit (WGM11) | bit (COM1B1); // fast PWM, reinicia OC1B comparación
  TCCR1B = bit (WGM12) | bit (WGM13) | bit (CS10);   // fast PWM, no prescaler
  OCR1A =  (F_CPU / 40000L) - 1;
  OCR1B = (F_CPU / 40000L) / 2;
  interrupts();             // habilita todas las interrupciones

  // deshabilitamos todo lo que no necesitamos
  ADCSRA = 0;  // ADC
  power_adc_disable ();
  power_spi_disable();
  power_twi_disable();
  power_timer0_disable();
  //power_usart0_disable();
  Serial.begin(115200);

 byte* emittingPointer = &animation[frame][0];
 byte buttonsPort = 0;

 bool anyButtonPressed;
 bool buttonPressed[N_BUTTONS];
 short buttonCounter = 0;

  LOOP:
    while(PINB & 0b00001000); //esperamos a que el pin 11 (B3) se encuentre en nivel bajo                         
    
    OUTPUT_WAVE(emittingPointer, 0); buttonsPort = PIND; WAIT_LIT();
    OUTPUT_WAVE(emittingPointer, 1); anyButtonPressed = (buttonsPort & 0b11111100) != 0b11111100; WAIT_LOT();
    OUTPUT_WAVE(emittingPointer, 2); buttonPressed[0] = buttonsPort & 0b00000100; WAIT_LOT();
    OUTPUT_WAVE(emittingPointer, 3); buttonPressed[1] = buttonsPort & 0b00001000; WAIT_LOT();
    OUTPUT_WAVE(emittingPointer, 4); buttonPressed[2] = buttonsPort & 0b00010000; WAIT_LOT();
    OUTPUT_WAVE(emittingPointer, 5); buttonPressed[3] = buttonsPort & 0b00100000; WAIT_LOT();
    OUTPUT_WAVE(emittingPointer, 6); buttonPressed[4] = buttonsPort & 0b01000000; WAIT_LOT();
    OUTPUT_WAVE(emittingPointer, 7); buttonPressed[5] = buttonsPort & 0b10000000; WAIT_LOT();
    OUTPUT_WAVE(emittingPointer, 8); WAIT_LOT();
    OUTPUT_WAVE(emittingPointer, 9); WAIT_LOT();
    OUTPUT_WAVE(emittingPointer, 10); WAIT_LOT();
    OUTPUT_WAVE(emittingPointer, 11); WAIT_LOT();
    OUTPUT_WAVE(emittingPointer, 12); WAIT_LOT();
    OUTPUT_WAVE(emittingPointer, 13); WAIT_LOT();
    OUTPUT_WAVE(emittingPointer, 14); WAIT_LOT();
    OUTPUT_WAVE(emittingPointer, 15); WAIT_LOT();
    OUTPUT_WAVE(emittingPointer, 16); WAIT_LOT();
    OUTPUT_WAVE(emittingPointer, 17); WAIT_LOT();
    OUTPUT_WAVE(emittingPointer, 18); WAIT_LOT();
    OUTPUT_WAVE(emittingPointer, 19); WAIT_LOT();
    OUTPUT_WAVE(emittingPointer, 20); WAIT_MID();
    OUTPUT_WAVE(emittingPointer, 21); WAIT_MID();
    OUTPUT_WAVE(emittingPointer, 22); WAIT_MID();
    OUTPUT_WAVE(emittingPointer, 23); WAIT_MID();
    OUTPUT_WAVE(emittingPointer, 24); WAIT_MID();
    OUTPUT_WAVE(emittingPointer, 25); WAIT_MID();
    OUTPUT_WAVE(emittingPointer, 26); WAIT_MID();
    OUTPUT_WAVE(emittingPointer, 27); WAIT_MID();
    OUTPUT_WAVE(emittingPointer, 28); WAIT_MID();
    OUTPUT_WAVE(emittingPointer, 29); WAIT_MID();
    OUTPUT_WAVE(emittingPointer, 30); WAIT_MID();
    OUTPUT_WAVE(emittingPointer, 31); WAIT_MID();
    OUTPUT_WAVE(emittingPointer, 32); WAIT_MID();
    OUTPUT_WAVE(emittingPointer, 33); WAIT_MID();
    OUTPUT_WAVE(emittingPointer, 34); WAIT_MID();
    OUTPUT_WAVE(emittingPointer, 35); WAIT_MID();
    OUTPUT_WAVE(emittingPointer, 36); WAIT_MID();
    OUTPUT_WAVE(emittingPointer, 37); WAIT_MID();
    OUTPUT_WAVE(emittingPointer, 38); WAIT_MID();
    OUTPUT_WAVE(emittingPointer, 39);
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
